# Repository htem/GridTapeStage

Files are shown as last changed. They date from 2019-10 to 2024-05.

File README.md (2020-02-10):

License
-----

Please note the [open-source license](LICENSE.md) before proceeding.

Files
-----

    docs/stage.md: description of stage
    docs/gridtape_stage.png: diagram of stage parts

    docs/protocol.md: description of command protocol and connection info
    docs/commands.md: description of commands, codes and options

    docs/tape_movement.png: diagram of stage movement states and transitions

    software/demo.py: demo python script
    software/temcagt: python control code

    firmware/temcagt_reel: arduino firmware

    docs/parts.xlsx: parts list for orings, fasteners, etc...
    docs/BOM_191002.xlsx: bill of materials including custom parts
    docs/pinouts.xlsx: drive electronics connector pinouts

    hardware/parts: design files for stage parts and assembly
    hardware/drawings: drawings of stage parts

    docs/assembly_instructions.pdf: electronics and hardware assembly
    docs/installation_instructions.pdf: installation instructions

Where to start
-----

Mechanical CAD files were designed in Solidworks and will require a modern (2016+)
version of Solidworks to view.

It's recommended to read through the files in the order they are listed above.

Construction of a stage will require fabricating or purchasing parts found in
the main assembly hardware/parts/xy_v2.SLDASM. Refer to the BOM for a detailed
list of where to purchase and/or how to fabricate components.

See docs/stage.md for a description of the stage.

Extensions to the microcope column (the piezo chamber and reel housings)
should be fabricated, cleaned in a method compatible with a high vacuum system,
assembled with flanges and oring seals and attached to the microscope to
test for leaks. Then, electronics should be added and tape movement tested.
Finally, the piezos, tape channel, pickup rest and a test piece of tape should
be installed to test montaging of tape.

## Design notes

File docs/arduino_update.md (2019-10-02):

Installation
======

IDE
====
The newest version (1.6.11) should be fine.
https://www.arduino.cc/en/Guide/HomePage

Libraries
====
You will also need to install three additional libraries.
https://www.arduino.cc/en/Guide/Libraries  see Manual Installation towards 
the bottom of the page

dSPIN
====
https://github.com/braingram/dSPIN

Comando
====
https://github.com/braingram/comando

HX711
====
https://github.com/bogde/HX711/tree/7ef05358e286980469da54ab3b6235102f44c4f2
The newest commits have changed the way the tension is read so use commit: 7ef05358e286980469da54ab3b6235102f44c4f2

Updating
======
Open the sketch temcagt_reel/temcagt_reel.ino in the Arduino IDE. Make sure 
the electronics are hooked up to the computer. Make sure the correct board 
is selected by checking Tools->Board, it should be something like Arduino Uno.
Make sure the correct port is selected in Tools->Port. Click the upload button.

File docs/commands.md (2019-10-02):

List of commands
------

```
<command_id> : <name> : brief description
    arguments : 
    --
    return values :

0 : error : an error occured in the tape movement
    error code [byte] (see below)

1 : ping : send/receive a simple code (test connection)
    code [byte] : an arbitrary code
    --
    code [byte] : an arbitrary code

5 : read_tension : read n_samples of the tension and return the mean
    n_samples [byte] : number of samples to average
    --
    tension_mean [int32] : result of the average

6 : set_led : set the led brightness
    brightness [byte] : (0 full on, 255 off)

10 : reset_drives : reconfigure all drives

12 : get_status : get the status word for a specific motor
    motor_code [byte] : see below
    --
    status_word [int16] : see below

15 : hold_drive : lock a drive in place
    motor_code [byte] : see below

16 : release_drive : release a drive to allow it to spin freely
    motor_code [byte] : see below

17 : rotate_drive : rotate a drive at a fixed number of steps per second
    motor_code [byte] : see below
    direction [byte] : (0 or 1)
    speed [float] : (steps per second)

18 : set_speed : set the maximum speed of a drive
    motor_code [byte] : see below
    speed [float] : (steps per second)

19 : get_speed : get the maximum speed of a drive
    motor_code [byte] : see below
    --
    speed [float] (steps per second)

20 : move_drive : move a drive a certain number of microsteps
    motor_code [byte] : see below
    direction [byte] : (0 or 1) see below
    n_steps [uint32] : number of microsteps to move

21 : run_reels : rotate both reel motors to take up slack at a fixed rpm
    rpm [float]

22 : stop_reels : stop both reel motors (release them)

23 : stop_all : stop motion of all motors (release reels, hold pinch drives)

24 : release_all : release all motors (allowing them to spin freely)

30 : step_tape : move both pinch drives to advance/retract the tape
    direction [byte] : tape direction
    feed_steps [uint32] : number of microsteps to move feed pinch drive
    pickup_steps [uint32] : number of microsteps to move pickup pinch drive
    time [float] : (seconds) duration of movement
    options [byte] : see below
```

Error Codes
------

- 0 : Error, generic error
- 1 : Missing argument, command call was missing a required argument
- 2 : Invalid argument, a command argument was invalid
- 10 : Invalid drive, a command received an invalid drive motor code
- 11 : Invalid direction, a command received an invalid tape direction

Motor Codes
------

Motor codes are bit fields that determine the side and type of motor to be used in a command. The first bit determines the type (0 reel motor, 1 pinch drive) and second determines the side (0 feed, 1 pickup). In total, the four motors are:

- 0b00 : Feed reel motor
- 0b01 : Feed pinch motor
- 0b10 : Pickup reel motor
- 0b11 : Pickup pinch motor

Tape direction
------

In total there are four tape directions (see 504 in temcagt_reel/reel.ino):

- 0 : Collect, send tape out of a side
- 1 : Dispense, pull tape into a side
- 2 : Tension, pull tape into both sides
- 3 : Untension, send tape out of both sides

Status Word
------

The status word is a 16 bit word read from the motor driver (L6470). See the [L6470 datasheet](www.st.com/resource/en/datasheet/l6470.pdf) for more information.

Step Tape Options
------

The step tape command takes an options byte that currently contains only 1 useful option:

- 0b10 : Wait, wait and report when the tape movement is finished

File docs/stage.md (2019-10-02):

Stage sides
------

The stage is seperated into two parts, a feed side (to the left/front when looking
at the microscope) and a pickup side (to the right/rear). Each side contains
two motors, a pinch drive that can move the tape a linear distance and a reel drive
that rotates to take up extra tape slack during movements.

Stage parts
------

Please see the diagram, gridtape_stage.png.

A. Objective pole piece of microscope
B. Reel motors (outside vacuum)
C. GridTape reels
D. Pinch motors (outside vacuum)
E. Pinch rollers
F. Idle rollers
G. Tension sensor
H. Piezo linear stages
I. Tape channel

The tape path starts at the feed reel (B left), goes between the idle and pinch rollers (E, F), over the tension sensor (G) and into the tape channel (I) that is affixed to the piezo stages (H). While in the channel the tape passes through the objective pole piece (A). From there, the tape exits the channel, enters the pickup pinch drive (right F, E) and is collected onto the pickup reel (right C).

Electronics
------

The stage electronics should be connected in the following order (starting with the power off):

1. connect the stepper motors (these should never be attached or detached when power is on)
2. connect the led and tension sensors (double check they are each in the correct port)
3. connect power
4. connect usb

If power is reset, be sure to disconnect and then reconnect the usb (to reset the arduino).

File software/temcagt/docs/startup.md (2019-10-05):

temcagt nodes are started, stopped and checked using the temcagt script in:

scripts/temcagt

After you install the temcagt python module, this script should be in your
PATH and available for use (note: if the module is installed as an egg-link
by passing -e to pip, you will need to reinstall the temcagt module after any
updates to the temcagt script).

To start the temcagt motion node run:

temcagt start motion

and a similar command for the camera node:

temcagt start camera

Running "temcagt start" without providing any node names will cause the temcagt
script to look in your ~/.temcagt/configs directory for all available node
config files (e.g. ~/.temcagt/configs/motion.json). The temcagt script will then
start all of these nodes in the appropriate order.

After nodes are running, their status can be checked with:

temcagt status

Example output might look like this:

temcagt pids are:
    camera: 22115
    control: 22219
    motion: 22146
    tape: 22189
    ui: 22250

Listing all running nodes and their associated process ids (pids).

To stop the motion node run:

temcagt kill motion

As with temcagt start, temcagt kill can be run with no node names.

If a node fails to kill after several attempts, a more severe stop signal
can be sent using "temcagt kill9". After a kill9 any child processes that
were started by the node will need to be manually killed. For example, if
a camera node fails to shut down after a kill and a kill9 is issued. Run
something like the following to check for remaining processes:

ps aux | grep camera | grep python | grep temcagt

Then kill the process ids using the kill command line tool:

kill 287403

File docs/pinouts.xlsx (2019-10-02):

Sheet: DB-9 pinouts
 | Pin Number | Signal | Stepper wire | Shield Input | Shield | Shield Signal | CS | Chain Index | 0 direction | Enclosure Port
Top DB-9 | 1 | Feed, Pinch | Red | ST2 | Top | 2B | A2 | 0 | CCW | Top
 | 2 | Feed, Pinch | Blue | ST2 | Top | 1B | A2 | 0 | CCW | Top
 | 3 | Feed, Pinch | Black | ST2 | Top | 1A | A2 | 0 | CCW | Top
 | 4 | Feed, Pinch | Green | ST2 | Top | 2A | A2 | 0 | CCW | Top
 | 5 | NC
 | 6 | Feed, Reel | Red | ST2 | Bottom | 2B | D2 | 0 | CCW | Top
 | 7 | Feed, Reel | Blue | ST2 | Bottom | 1B | D2 | 0 | CCW | Top
 | 8 | Feed, Reel | Black | ST2 | Bottom | 1A | D2 | 0 | CCW | Top
 | 9 | Feed, Reel | Green | ST2 | Bottom | 2A | D2 | 0 | CCW | Top
Bottom DB-9 | 1 | Pickup, Pinch | Red | ST1 | Top | 2B | A2 | 1 | CCW | Bottom
 | 2 | Pickup, Pinch | Blue | ST1 | Top | 1B | A2 | 1 | CCW | Bottom
 | 3 | Pickup, Pinch | Black | ST1 | Top | 1A | A2 | 1 | CCW | Bottom
 | 4 | Pickup, Pinch | Green | ST1 | Top | 2A | A2 | 1 | CCW | Bottom
 | 5 | NC
 | 6 | Pickup, Reel | Red | ST1 | Bottom | 2B | D2 | 1 | CCW | Bottom
 | 7 | Pickup, Reel | Blue | ST1 | Bottom | 1B | D2 | 1 | CCW | Bottom
 | 8 | Pickup, Reel | Black | ST1 | Bottom | 1A | D2 | 1 | CCW | Bottom
 | 9 | Pickup, Reel | Green | ST1 | Bottom | 2A | D2 | 1 | CCW | Bottom

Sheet: 4 pin pinouts
 | Pin number | Signal | Buckpuck | Arduino | Load cell | Lemo Pin | Lemo Color
Left 4 pin | 1 | E+ |  |  | Red | 9 | Grey
(above USB) | 2 | E- |  |  | Black | 8 | Violet
 | 3 | A- |  |  | White | 7 | Blue
 | 4 | A+ |  |  | Green | 10 | White
Right 4 pin | 1 | 12V | V+ | -
 | 2 | 5V | REF
 | 3 | D3 | CTL | D3
 | 4 | GND | V- | GND

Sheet: 10pin Lemo
Pin | Wire color | Signal | Load Cell | 4 Pin connector
1 | Black
2 | Brown
3 | Red
4 | Orange
5 | Yellow
6 | Green
7 | Blue | A- | White | 3
8 | Violet | GND (E-) | Black | 2
9 | Gray | 5V (E+) | Red | 1
10 | White | A+ | Green | 4

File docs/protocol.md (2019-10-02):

Hardware Interface
------

The lowest level of interface to the control electronics is a serial
connection running at 115200 baud. A connection to this interface can
be made with pyserial and uses the default connection parameters of

- bytesize=8
- parity='N'
- stopbits=1
- xonxoff=False
- rtscts=False
- dsrdtr=False

```python
import serial

conn = serial.Serial('/dev/ttyACM0', 115200)
```

On connection, the arduino will reset and needs a few (3-4) seconds
to start up before it is able to receive commands.

Message Protocol
------

The serial communication uses a standard message format, part of the
[comando](http://github.com/braingram/comando) library, to allow for
efficient and flexible passing of data back and forth between the
host computer and the control electronics. The low level messages
are described [here](https://github.com/braingram/comando/blob/master/doc/messages.md)
on top of which is built a [protocol format] (https://github.com/braingram/comando/blob/master/doc/protocols.md)
which is used to transmit command following a [command format](https://github.com/braingram/comando/blob/master/doc/commands.md).

These ability to use the same connection for multiple protocols is current not
used. Currently all interaction is through the command protocol which
can be setup as follows:

```python
import pycomando
import serial

conn = serial.Serial('/dev/ttyACM0', 115200)
com = pycomando.Commando(conn)
cmd = pycomando.protocols.CommandProtocol(com)

com.register_protocol(1, cmd)
```

A detailed example of using pycomando commands can be found [here](https://github.com/braingram/comando/blob/master/examples/commands.py). Although the pycomando module is open source,
it is not necessary to use the pycomando module. Briefly, commands can
be sent as follows:

```python
# sent a command of command_id wih 3 arguments (arg0, arg1, arg2)
cmd.send_command(command_id, (arg0, arg1, arg2))

# send a command 0, with args True, 1, 1.5
cmd.send_command(0, (True, 1, 1.5))
```

Receiving commands is done through a callback system.

```python
def ping_received(cmd):
    print("ping received")

# when a command of id 0 is received, call ping_received
cmd.register_callback(0, ping_received)
```

Updating the Comando instance to check for new serial data is done
explicitly by calling: 

```python
com.handle_stream()
```

Additionally, the commands can be called through an EventManager instance
which when initialized with a description of the commands (like that in
the demo, lines 45-142) gives name-based access to commands. For example,
to stop movement of all the motors run:

```python
mgr.trigger('stop_all')
```

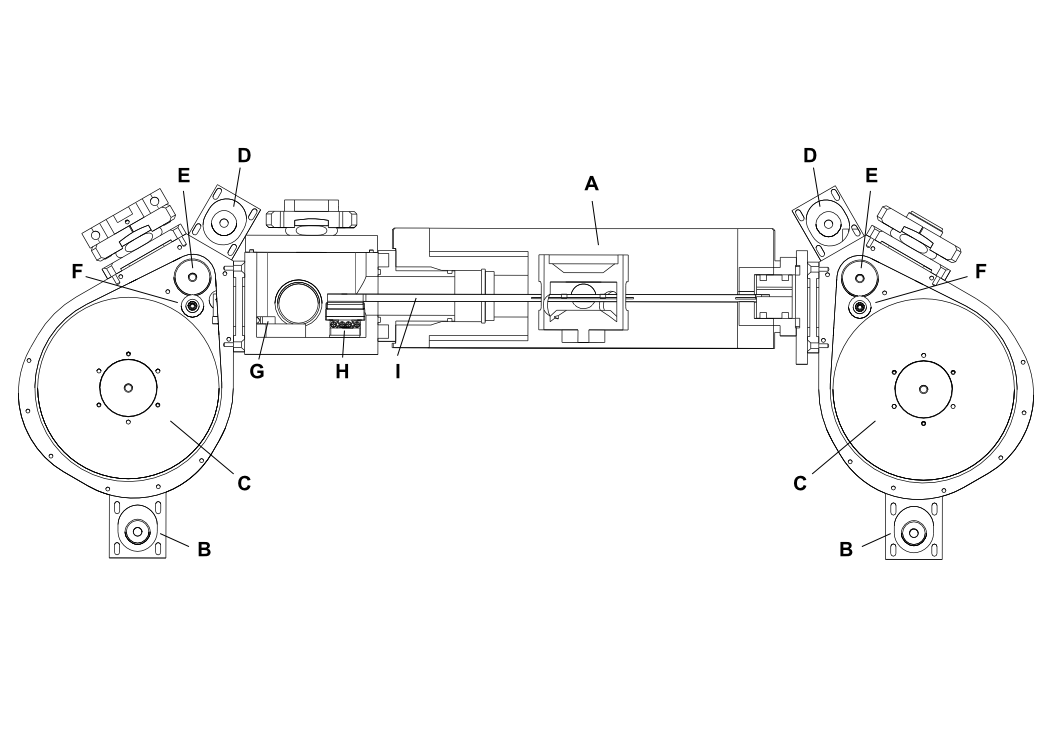
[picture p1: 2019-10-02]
docs/gridtape_stage.png

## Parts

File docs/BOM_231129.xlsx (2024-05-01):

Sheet: BOM
Part name | Quantity | CAD file | Drawing | Assembly | Type | Tested? | Info | Operation | Vender | Part Number | Quantity for 2 | Link | Package Cost | Units per package | Cost (for 1) | Packages for 2 | Cost | Ordered | When
chamber | 1 | chamber_v1 | chamber_v1 | piezo chamber | custom | yes | Al, 2 x 2.25 x 2.938 | machine |  |  | 2
chamber lid | 1 | chamber_lid_with_view | chamber_lid_with_view | piezo chamber | custom | yes | Al, 3/8 x 2 x 2.9063 | machine |  |  | 2
front left flange | 1 | front_left_xy_flange | front_left_xy_flange | piezo chamber | custom |  | Al, 1.6937 x 2 x 2.75 | machine |  |  | 2
piezo baseplate | 1 | piezo_baseplate | piezo_baseplate | piezo stack | custom | yes | Al, 0.049 x 0.669 x 1.181 | machine |  |  | 2
channel baseplate | 1 | channel_base_plate | channel_baseplate | piezo stack | custom | yes | Al, 0.0705 x 0.669 x 0.787 | machine |  |  | 2
load cell baseplate | 1 | load_cell_vertical_base_v2 | load_cell_vertical_base_v2 | tension sensor | custom | yes | Al, 0.295 x 0.570 x 0.875 | machine |  |  | 2
load cell adapter | 1 | tension_roller_mount_v2 | tension_roller_mount_v2 | tension sensor | custom | yes | Al, 0.25 x 0.5 x 0.647 | machine |  |  | 2
load cell rollers | 1 | tension_roller_v2 | tension_roller_v2 | tension sensor | custom | yes | Al, D0.25 x 0.5 | machine |  |  | 2
channel bottom | 1 | straight_stick_v2 | straight_stick_v2 | channel | custom | yes | Al, 1.575 x 0.6693 x 9.75 | machine |  |  | 2
tape clamp | 1 | tape_clamp | tape_clamp | channel | custom | yes | Al, 0.0787 x 0.315 x 9.75 | machine |  |  | 2
takeup reel flange | 1 | takeup_reel_flange | takeup_reel_flange | takeup | custom | yes | Al, 0.25 x 2.5 x 2.5 | machine |  |  | 2
takeup rest static insert | 1 | takeup_rest_insert | takeup_rest_insert | takeup | custom | yes | SS, D1.322 x 0.7874 | machine |  |  | 2
reel housing | 2 | reel_housing | reel_housing | reel housing | custom | yes | Al, 1.25 x 4.625 x 5.8956 | machine |  |  | 4
reel door | 2 | reel_door | reel_door | reel housing | custom | yes | Al, 0.25 x 4.625 x 5.8956 | machine |  |  | 4
reel flange | 2 | reel_housing_flange | reel_housing_flange | reel housing | custom | yes | Al, 0.25 x 2 x 2 | machine |  |  | 4
reel to qf flange | 2 | reel_housing_to_qf16_flange | reel_to_qf16_flange | reel housing | custom | yes | Al, 0.25 x 2 x 2 | machine |  |  | 4
reel blank flange | 4 | reel_housing_blank | reel_housing_blank | reel housing | custom | yes | Al, 0.25 x 1.25 x 2 | machine |  |  | 8
idle roller | 2 | roller | roller | reel housing | custom | yes | Al, D0.5 x 0.4478 | emachineshop |  |  | 4
roller spacer |  | roller_spacer |  | reel housing | custom | yes | Al | machine
inner spacer |  | inner_spacer |  | reel housing | custom | yes | Al | machine
pinch drive roller | 4 | drive_roller | drive_roller | pinch drive | custom | yes | Al, D0.82 x 0.315 | machine |  |  | 8
smaller pinch drive roller | 2 | drive_roller_smaller |  | pinch drive | custom | yes | Al, D0.81 x 0.315 | machine |  |  | 4
pinch drive plate | 2 | pinch_drive_clamp_short |  | pinch drive | custom | yes | Al, 0.125 x 1.1024 x 1.4824 | waterjet |  |  | 4
reel adapter | 2 | reel_adapter_screw_set_3f16 | reel_adapter_screw_set_3f16 | reel drive | custom | yes | Al, D1.675 x 0.5 | machine |  |  | 4
reel drive feedthrough clamp | 4 | ferrotec_clamp | ferrotec_clamp | reel drive | custom | yes | Al, 0.1875 x 1.1024 x 1.1024 | machine |  |  | 8
reel drive plate | 2 | reel_drive_clamp_slipclutch |  | reel drive | custom | yes | Al, 0.125 x 4.4973 x 5.167 | waterjet |  |  | 4
slip clutch shaft | 2 | shaft_adapter_slipclutch | shaft_adapter_slipclutch | reel drive | custom | yes | Al, D0.5 x 1 | machine |  |  | 4
takeup rest oring | 2 |  |  | takeup | oring |  | dash 122 | order | mcmaster | 9464K86 | 4 | http://www.mcmaster.com/#9464K86 | 11.63 | 50 | 0.2326 | 1 | 11.63
piezo chamber lid oring | 1 |  |  | piezo chamber | oring | yes | dash 036 | order | mcmaster | 9464K361 | 2 | http://www.mcmaster.com/#9464K361 | 4.75 | 10 | 0.475 | 1 | 4.75
front left to piezo oring | 1 |  |  | piezo chamber | oring |  | dash 027 | order | mcmaster | 9464K271 | 2 | http://www.mcmaster.com/#9464K271 | 10.76 | 50 | 0.2152 | 1 | 10.76
front left to scope oring | 1 |  |  | piezo chamber | oring |  | dash 028 | order | mcmaster | 9464K281 | 2 | http://www.mcmaster.com/#9464K281 | 10.49 | 50 | 0.2098 | 1 | 10.49
reel flange oring | 6 |  |  | reel housing | oring | yes | dash 027 | order | mcmaster | 9464K271 | 12 | http://www.mcmaster.com/#9464K271 | 10.76 | 50 | 0.2152 | 1 | 10.76
takeup flange oring | 1 |  |  | takeup | oring | yes | dash 219 | order | mcmaster | 9464K41 | 2 | http://www.mcmaster.com/#9464K41 | 11.25 | 25 | 0.45 | 1 | 11.25 |  |  | 92010A001
pinch drive oring | 4 |  |  | pinch drive | oring | yes | dash 018 square | order | mcmaster | 1170N29 | 8 | http://www.mcmaster.com/#1170N29 | 7.94 | 10 | 0.794 | 1 | 7.94 | 6448208 | 2016-03-22
reel housing door oring | 2 |  |  | reel housing | oring | yes | dash 048 | order | mcmaster | 9464K511 | 4 | http://www.mcmaster.com/#9464K511 | 2.23 | 2 | 1.115 | 2 | 4.46 | 6448208 | 2016-03-22
QF-25 clamp | 2 |  |  | piezo chamber | flange | yes |  | order | lesker | QF25-100-C | 4 | http://www.lesker.com/newweb/flanges/hardware_kf_clamps_machined.cfm?pgid=al2 | 8.25 | 1 | 8.25 | 4 | 33 | 6381132 | 160201
QF-25 centering ring | 3 |  |  | piezo chamber | flange | yes |  | order | lesker | QF25-100-SRV | 6 | http://www.lesker.com/newweb/flanges/hardware_kf_centeringrings.cfm?pgid=ss | 8.25 | 1 | 8.25 | 6 | 49.5 | 6381132 | 160201
QF-25 tee | 1 |  |  | piezo chamber | flange | yes |  | order | lesker | QF25-100-T | 2 | http://www.lesker.com/newweb/flanges/fittings_kf_tees.cfm?pgid=standardtee | 75 | 1 | 75 | 2 | 150 | 6381132 | 160201
QF-25 blank flange | 2 |  |  | piezo chamber | flange | yes |  | order | lesker | QF25-100-SB | 4 | http://www.lesker.com/newweb/flanges/flanges_kf_blank.cfm?pgid=flange1 | 9.3 | 1 | 9.3 | 4 | 37.2 | 6381132 | 160201
QF-25 bulkhead clamp | 1 |  |  | piezo chamber | flange | yes |  | order | lesker | QF25-100-BC | 2 | http://www.lesker.com/newweb/flanges/hardware_kf_clamps_bulkhead.cfm?pgid=al | 21.8 | 1 | 21.8 | 2 | 43.6 | 6381132 | 160201
QF-25 feedthrough (smaract) | 1 |  |  | piezo chamber | flange | yes |  | modify | lesker | QF25-100-SB | 2 | http://www.lesker.com/newweb/flanges/flanges_kf_blank.cfm?pgid=flange1 | 9.3 | 1 | 9.3 | 2 | 18.6 | 6381132 | 160201
QF-25 feedthrough (tension) | 1 |  |  | piezo chamber | flange | yes |  | modify | lesker | QF25-100-SB | 2 | http://www.lesker.com/newweb/flanges/flanges_kf_blank.cfm?pgid=flange1 | 9.3 | 1 | 9.3 | 2 | 18.6 | 6381132 | 160201
QF-16 viewport | 3 |  |  | reel housing | flange | yes |  | order | lesker | QF16-075-VP | 6 | http://www.lesker.com/newweb/flanges/viewports_kf_glass.cfm?pgid=0 | 100 | 1 | 100 | 6 | 600 | 6381132 | 160201
QF-16 blank | 3 |  |  | reel housing | flange | yes |  | order | lesker | QF16-075-SB | 6 | http://www.lesker.com/newweb/flanges/flanges_kf_blank.cfm?pgid=flange1 | 8.25 | 1 | 8.25 | 6 | 49.5 | 6381132 | 160201
QF-16 centering ring | 3 |  |  | reel housing | flange | yes |  | order | lesker | QF16-075-SRV | 6 | http://www.lesker.com/newweb/flanges/hardware_kf_centeringrings.cfm?pgid=ss | 6.5 | 1 | 6.5 | 6 | 39 | 6381132 | 160201
QF-16 bulkhead clamp | 3 |  |  | reel housing | flange | yes |  | order | lesker | QF16-075-BC | 6 | http://www.lesker.com/newweb/flanges/hardware_kf_clamps_bulkhead.cfm?pgid=al | 18.6 | 1 | 18.6 | 6 | 111.6 | 6381132 | 160201
tension sensor roller pin | 1 |  |  | tension sensor | fastener | yes | SS, 1/8 x 5/16 dowel pin | order | mcmaster | 90145A878 | 2 | http://www.mcmaster.com/#90145A878 | 7.34 | 50 | 0.1468 | 1 | 7.34
tension sensor adapter screws | 4 |  |  | tension sensor | fastener |  | SS, 0-80 x 1/4 FH | order | mcmaster | 91771A055 | 8 | http://www.mcmaster.com/#91771A055 | 9.01 | 100 | 0.0901 | 1 | 9.01
tension sensor mounting screws | 2 |  |  | tension sensor | fastener | yes | SS, 2-56 x 3/8 SHCS vented | order | mcmaster | 93235A079 | 4 | http://www.mcmaster.com/#93235A079 | 8.12 | 5 | 1.624 | 1 | 8.12 | 6448208 | 2016-03-22
piezo baseplate mounting screws | 4 |  |  | piezo chamber | fastener | yes | SS, 2-56 x 3/16 SHCS vented | order | mcmaster | 93235A076 | 8 | http://www.mcmaster.com/#93235A076 | 5.35 | 5 | 1.07 | 2 | 10.7 | 6448208 | 2016-03-22
piezo stack mounting screws | 4 |  |  | piezo chamber | fastener |  | SS, M1.6 x 4 mm FH | order | mcmaster | 91430A003 | 8 | http://www.mcmaster.com/#91430A003 | 8.7 | 25 | 0.348 | 1 | 8.7 | 6448208 | 2016-03-22
channel plate mounting screws | 2 |  |  | piezo chamber | fastener |  | SS, M2 x 4 mm FH | order | mcmaster | 92010A001 | 4 | http://www.mcmaster.com/#92010A001 | 4 | 100 | 0.04 | 1 | 4
channel mounting screws | 4 |  |  | channel | fastener |  | SS, 0-80 x 7/32 FH | order | mcmaster | 91771A040 | 8 | http://www.mcmaster.com/#91771A040 | 9.63 | 100 | 0.0963 | 1 | 9.63
front left to column screws | 4 |  |  | piezo chamber | fastener |  | SS, M6 x 10 SHCS low profile | order | mcmaster | 92855A610 | 8 | http://www.mcmaster.com/#92855A610 | 8.21 | 25 | 0.3284 | 1 | 8.21 | 6448208 | 2016-03-22
chamber to front left screws | 4 |  |  | piezo chamber | fastener |  | SS, M5 x 16 SHCS | order | mcmaster | 91292A126 | 8 | http://www.mcmaster.com/#91292A126 | 10 | 100 | 0.1 | 1 | 10
chamber lid screws | 4 |  |  | piezo chamber | fastener |  | SS, 6-32 x 1/2 FHSC | order | mcmaster | 92210A148 | 8 | http://www.mcmaster.com/#92210A148 | 4.36 | 100 | 0.0436 | 1 | 4.36
reel flange small screws | 16 |  |  | reel housing | fastener |  | SS, 4-40 x 3/8 FHSC | order | mcmaster | 92210A108 | 32 | http://www.mcmaster.com/#92210A108 | 3.35 | 100 | 0.0335 | 1 | 3.35 | 6448208 | 2016-03-22
reel flange large screws | 16 |  |  | reel housing | fastener |  | SS, 6-32 x 7/16 FHSC | order | mcmaster | 92210A114 | 32 | http://www.mcmaster.com/#92210A114 | 4.38 | 100 | 0.0438 | 1 | 4.38 | 6448208 | 2016-03-22
idle roller shoulder screw | 2 |  |  | pinch drive | fastener |  | SS, 4-40 x 1/8 x 5/8 shoulder screw | modify | mcmaster | 97345A104 | 4 | http://www.mcmaster.com/#97345A104 | 4.39 | 1 | 4.39 | 4 | 17.56 | 6448208 | 2016-03-22
pinch roller set screws | 4 |  |  | pinch drive | fastener |  | SS, 8-32 x 1/4 set screw vented | order | mcmaster | 91979A408 | 8 | http://www.mcmaster.com/#91979A408 | 7.1 | 10 | 0.71 | 1 | 7.1 | 6448208 | 2016-03-22
reel drive set screw | 2 |  |  | reel drive | fastener |  | SS, 8-32 x 1/4 set screw vented | order | mcmaster | 91979A408 | 4 | http://www.mcmaster.com/#91979A408 | 7.1 | 10 | 0.71 | 1 | 7.1 | 6448208 | 2016-03-22
reel hub screws | 6 |  |  | reel drive | fastener |  | SS, 2-56 x 1/2 SHCS | order | mcmaster | 92196A081 | 12 | http://www.mcmaster.com/#92196A081 | 5.72 | 100 | 0.0572 | 1 | 5.72 | 6448208 | 2016-03-22
reel door screws | 20 |  |  | reel housing | fastener | yes | SS, 4-40 x 3/8 SHCS | order | mcmaster | 92196A108 | 40 | http://www.mcmaster.com/#92196A108 | 3.98 | 100 | 0.0398 | 1 | 3.98 | 6448208 | 2016-03-22
ferrotec slamp screws | 16 |  |  | reel housing | fastener |  | SS, 2-56 x 5/16 FHSC | order | mcmaster | 92210A078 | 32 | http://www.mcmaster.com/#92210A078 | 6.22 | 100 | 0.0622 | 1 | 6.22
drive clamp screws | 6 |  |  | reel housing | fastener |  | SS, 4-40 x 3/8 SHCS | order | mcmaster | 92196A108 | 12 | http://www.mcmaster.com/#92196A108 | 3.98 | 100 | 0.0398 | 1 | 3.98 | 6448208 | 2016-03-22
nema 11 screws | 16 |  |  | reel housing | fastener | yes | SS, M2.5 x 6 BHSCS | order | mcmaster | 92095A458 | 32 | http://www.mcmaster.com/#92095A458 | 7.07 | 25 | 0.2828 | 2 | 14.14 | 6448208 | 2016-03-22
slip clutch set screws | 2 |  |  | reel drive | fastener |  | SS, 4-40 x 1/8 set screw | order | mcmaster | 92311A103 | 4 | http://www.mcmaster.com/#92311A103 | 4.21 | 100 | 0.0421 | 1 | 4.21 | 6448208 | 2016-03-22
takeup flange screws | 2 |  |  | takeup | fastener |  | SS, M4 x 10 FHSC | order | mcmaster | 92125A190 | 4 | http://www.mcmaster.com/#92125A190 | 7.23 | 100 | 0.0723 | 1 | 7.23
takeup flange wrench | 1 |  |  | takeup | tool |  | extended t-handle | order | mcmaster | 5334A42 | 2 | http://www.mcmaster.com/#5334A42 | 1.97 | 1 | 1.97 | 2 | 3.94 | 6448208 | 2016-03-22
stepper motors | 4 |  |  | motors | motors |  | nema 11 stepper | order | digikey | 1460-1072-ND | 8 | http://www.digikey.com/product-search/en?keywords=1460-1072-nd | 37.99 | 1 | 37.99 | 8 | 303.92 | 6390515 | 160208
tension sensor | 1 |  |  | tension sensor | sensor |  | 0-100g load cell | modify | phidgets | CZL639HD | 2 | http://www.phidgets.com/products.php?category=34&product_id=3139_0 | 7 | 1 | 7 | 2 | 14 | pcard | 160205
ferrotec feedthrough | 4 |  |  | reel housing | feedthrough | yes | rotary feedthroughs |  | ferrotec | 103073 | 8 | https://www.ferrotec.com/index.php?id=feedthrough_detail&vfp_id=34 | 600 | 1 | 600 | 8 | 4800 | 6382708 | 160202
piezo xy stack | 1 |  |  | piezo stack | motors |  | slc-1720-s-hv, in xy, with MCS | order | smaract | slc-1720-s-hv | 2 | http://smaract.de/index.php/products/slc17-positioners/slc-1720 | 9052.5 | 1 | 9052.5 | 2 | 18105 | 6382658 | 160202
load cell amplifier | 1 |  |  | electronics | electronics |  | load cell amplifier | modify | sparkfun | SEN-13230 | 2 | https://www.sparkfun.com/products/13230 | 9.95 | 1 | 9.95 | 2 | 19.9
microcontroller proto board | 1 |  |  | electronics | electronics |  | arduino protoshield | modify | sparkfun | DEV-11665 | 1 | https://www.sparkfun.com/products/11665 | 4.95 | 1 | 4.95 | 1 | 4.95
stepper motor driver shield | 2 |  |  | electronics | electronics |  | x-nucleo-ihm02a1 | modify | digikey | 497-16251-ND | 4 | https://punchout.digikey.com/scripts/DkSearch/dksus.dll?Detail&itemSeq=191838508&uq=635932000139947652 | 14.16 | 1 | 14.16 | 4 | 56.64 | 6432645 | 160310
power supply | 1 |  |  | electronics | electronics |  | 12V >3A supply | order | digikey | 237-1443-ND | 2 | http://www.digikey.com/product-detail/en/WSU120-3000/237-1443-ND/3094969 | 20.27 | 1 | 20.27 | 2 | 40.54 | 6390515 | 160208
power jack | 1 |  |  | electronics | electronics |  | barrel jack | modify | digikey | CP-065A-ND | 2 | http://www.digikey.com/product-search/en?keywords=CP-065A-ND | 2.54 | 1 | 2.54 | 2 | 5.08 | 6390515 | 160208
microcontroller | 1 |  |  | electronics | electronics |  | arduino | modify | digikey | 1050-1041-ND | 2 | http://www.digikey.com/product-detail/en/A000073/1050-1041-ND/3476357 | 21.54 | 1 | 21.54 | 2 | 43.08 | 6390515 | 160208
tension sensor cabling | 1 |  |  | electronics | electronics |  | 10 conductor wiring | modify | digikey | W410-50-ND | 1 | http://www.digikey.com/product-search/en?keywords=w410-50-nd | 64.63 | 1 | 64.63 | 1 | 64.63 | 6390515 | 160208
tension sensor feedthrough | 1 |  |  | electronics | electronics |  | lemo feedthrough | modify | mouser | 736-HGP2S310CLLPV | 2 | http://www.mouser.com/ProductDetail/LEMO/HGP2S310CLLPV/ | 102.14 | 1 | 102.14 | 2 | 204.28 | pcard | 160208
tension sensor connector | 1 |  |  | electronics | electronics |  | lemo plug | modify | mouser | 736-FFP2S310CLAC72Z | 2 | http://www.mouser.com/ProductDetail/LEMO/FFP2S310CLAC72Z/ | 70.11 | 1 | 70.11 | 2 | 140.22 | pcard | 160208
idle roller bearing | 4 |  |  | pinch drive | mechanics |  | 1/8 shaft 1/4 flanged bearing | order | mcmaster | 57155k205 | 8 | http://www.mcmaster.com/#57155K205 | 5.71 | 1 | 5.71 | 8 | 45.68 | 6448208 | 2016-03-22
pinch drive timing belt pulley | 4 |  |  | pinch drive | mechanics |  | 1/8 MXL 15 tooth 3/16 bore | modify | mcmaster | 1375K15 | 8 | http://www.mcmaster.com/#1375K15 | 9.81 | 1 | 9.81 | 4 | 39.24 | 6448208 | 2016-03-22
reel drive timing belt pulley | 2 |  |  | reel drive | mechanics |  | 1/8 MXL 15 tooth 3/16 bore | modify | mcmaster | 1375K15 | 4 | http://www.mcmaster.com/#1375K15 | 9.81 | 1 | 9.81 | 2 | 19.62 | 6448208 | 2016-03-22
slip clutch timing belt pulley | 2 |  |  | reel drive | mechanics |  | 1/8 MXL 18 tooth 3/16 bore | modify | mcmaster | 1375K17 | 4 | https://www.mcmaster.com/1375K17/ | 12.92 | 1 | 12.92 | 4 | 51.68
pinch drive timing belt | 1 |  |  | pinch drive | mechanics |  | MXL 1/8" Width, 4" Outer Circle | order | mcmaster | 7887K12 | 2 | http://www.mcmaster.com/#7887K12 | 2.39 | 1 | 2.39 | 2 | 4.78 | 6448208 | 2016-03-22
reel drive timing belt | 1 |  |  | reel drive | mechanics |  | MXL 1/8" Width, 7.6" Outer Circle | order | mcmaster | 7887K19 | 2 | http://www.mcmaster.com/#7887K19 | 2.51 | 1 | 2.51 | 2 | 5.02 | 6448208 | 2016-03-22
slip clutch | 2 |  |  | reel drive | mechanics |  | 0.25" Bore Adjustable Slip Clutch with Torque Range of .3 to 32 OZ-IN | order | SDP/SI | S98CA6-MEC160417 | 4 | https://shop.sdp-si.com/catalog/product/?id=S98CA6-MEC160417 | 64.59 | 1 | 64.59 | 2 | 129.18
tape camera | 1 |  |  | electronics | electronics |  | raspberry pi or m12 | order |  |  | 2 |  |  | 1 | 0 | 2 | 0
tape camera mount | 1 | picam_to_viewport_mount |  | tape camera | mechanics |  |  | 3d print |  |  | 2 |  | 0 | 1 | 0 | 2 | 0
light led | 1 |  |  | electronics | electronics |  |  | order | digikey |  | 2 |  |  | 1 | 0 | 2 | 0
light heatsink | 1 |  |  | electronics | electronics |  |  | order | digikey | 345-1105-ND | 2 | http://www.digikey.com/product-detail/en/882-100AB/345-1105-ND/2640528 | 2.34 | 1 | 2.34 | 2 | 4.68 | 6390515 | 160208
light driver | 1 |  |  | electronics | electronics |  |  | order | digikey | 788-1096-ND | 2 | http://www.digikey.com/product-detail/en/3021-D-I-700/788-1096-ND/3114413 | 16.99 | 1 | 16.99 | 2 | 33.98 | 6390515 | 160208
tc led mount | 1 | tc led mount |  |  | electronics |  |  | 3d print |  |  | 2 |  | 0 | 1 | 0 | 2 | 0
case | 1 |  |  | electronics | electronics |  |  | modify | digikey | HM856-ND | 2 | https://punchout.digikey.com/scripts/DkSearch/dksus.dll?Detail&itemSeq=193471005&uq=635950280810903346 | 7.94 | 1 | 7.94 | 2 | 15.88
db9 connector | 2 |  |  | electronics | electronics |  |  | order | digikey | L77SDE09S-ND | 4 | https://www.digikey.com/en/products/detail/amphenol-cs-commercial-products/L77SDE09S/1930962
db9 case | 1 |  |  | electronics | electronics |  |  | order | digikey | 116-40-9709H-ND | 2 | https://www.digikey.com/en/products/detail/cinch-connectivity-solutions/40-9709H/3830261
4 pin molex connector | 2 |  |  | electronics | electronics |  |  | order | digikey | 23-0022057045-ND | 4 | https://www.digikey.com/en/products/detail/molex/0022057045/403343
4 pin molex connector | 2 |  |  | electronics | electronics |  |  | order | digikey | WM17405-ND | 4 | https://www.digikey.com/en/products/detail/molex/0050375043/259392
molex crimps | 100 |  |  | electronics | electronics |  |  | order | digikey | WM18889CT-ND | 200 | https://www.digikey.com/en/products/detail/molex/0008701039/765268
7pos housing receptacle |  |  |  | electronics | electronics |  |  | order | digikey | 952-2232-ND | 25 | https://www.digikey.com/en/products/detail/harwin-inc/M20-1060700/3728196?s=N4IgTCBcDaILZgAwFoCMiBsiDsIC6AvkA
Harwin crimps |  |  |  | electronics | electronics |  |  | order | digikey | 952-2157-1-ND | 200 | https://www.digikey.com/en/products/detail/harwin-inc/M20-1160042/3728123

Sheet: Piezo Chamber
Part name | Info | Quantity | CAD file | Modification? | Vender | Part Number | Link | Package Cost | Units per package | Cost (for 1) | Cost | Ordered | When
chamber | Sheet 2 1/2 x 3 x 4 Al | 1 | chamber_v1 | Yes | mcmaster |  |  |  | 1 |  | #VALUE! | Yes | 150326
chamber lid | Sheet 3/8 x 2 1/2 x 6 Al | 1 | chamber_lid_with_view | Yes | mcmaster |  |  |  | 2 |  | #VALUE! | Yes | 150326
piezo baseplate | Sheet 1/8 x 1 x 6 Al | 1 | piezo_baseplate | Yes | mcmaster | 8975K578 | http://www.mcmaster.com/#8975k578 | 0.86 | 3 | $0.29 | $0.29 | Yes | stock
load cell baseplate | Sheet 1/2 x 1/2 x 6 Al | 1 | load_cell_vertical_base_v2 | Yes | mcmaster | 9008K81 | http://www.mcmaster.com/#9008k81 | 1.48 | 6 | $0.25 | $0.25 | Yes | stock
load cell wall | Sheet 0.032 x 2 x 24 Al | 2 | load_cell_plate | Yes | mcmaster | 89015k151 | http://www.mcmaster.com/#89015k151 | 5.2 | 24 | $0.22 | $0.43 | Yes | stock
load cell adapter | Sheet 1/2 x 1/2 x 6 Al | 1 | load_cell_roller_mount_v2 | Yes | mcmaster | 9008K81 | http://www.mcmaster.com/#9008k81 | 1.48 | 6 | $0.25 | $0.25 | Yes | stock
idle roller | Rod 5/16 x 6 Al | 2 | tension_roller_v2 | Yes | mcmaster | 8974k23 | http://www.mcmaster.com/#8974k23 | 1.9 | 6 | $0.32 | $0.63 | Yes | 150326
 |  | 1 | front_left_xy_flange
takeup rest | Rod 1 3/16 x 6 Al | 1 | takeup_rest_insert | Yes | mcmaster | 8974k17 | http://www.mcmaster.com/#8974k17 | 10.26 | 3 | $3.42 | $3.42
 |  |  | takeup_rest_body
 |  |  | takeup_rest_slider
channel bottom | Sheet 3/4 x 1 x 12 Al | 1 | straight_stick_v2 | Yes | mcmaster | 8975k11 | http://www.mcmaster.com/#8975k11 | 5.14 | 1 | $5.14 | $5.14 | Yes | 150401
 |  |  | channel_base_plate
channel top | Sheet 3/4 x 1 x 12 Al | 1 | tape_clamp | Yes | mcmaster | 8975k11 | http://www.mcmaster.com/#8975k11 | 5.14 | 1 | $5.14 | $5.14 | Yes | 150401
channel clamps | Shim 0.005 SS | 1 |  | Yes | mcmaster |  |  |  |  |  | #VALUE! | Yes | stock
-- fasteners -- |  |  |  |  |  |  |  |  |  |  | #VALUE!
tension roller pin
chamber mounting screws | M5 x 16 | 4 |  |  | mcmaster | 91292a126 | http://www.mcmaster.com/#91292a126 | 10 | 100 | $0.10 | $0.40 | Yes | stock
chamber lid screws | #6 x 1/2 fhsc | 4 |  |  | mcmaster | 92210a148 | http://www.mcmaster.com/#92210a148 | 4.92 | 100 | $0.05 | $0.20 | Yes | 150326
piezo baseplate screws | 2-56 x 3/16 sc vented | 4 |  |  | mcmaster | 93235a076 | http://www.mcmaster.com/#93235a076 | 5.35 | 5 | $1.07 | $4.28 | Yes | 150326
load cell wall screws | 0-80 x 1/8 sc | 4 |  | Yes | mcmaster | 92210a010 | http://www.mcmaster.com/#92210a010 | 4.58 | 50 | $0.09 | $0.37 | Yes | 150326
load cell base screws | 2-56 x 1/2 sc vented | 2 |  |  | mcmaster | 93235a081 | http://www.mcmaster.com/#93235a081 | 14.07 | 5 | $2.81 | $5.63 | Yes | stock
load cell adapter screws | 0-80 x 1/4 sc | 4 |  | Yes | mcmaster | 90585a017 | http://www.mcmaster.com/#90585a017 | 7.51 | 12 | $0.63 | $2.50 | Yes | 150326
channel mount screws | M2 x 3 fhsc | 2 |  |  | mcmaster | 93395a135 | http://www.mcmaster.com/#93395a135 | 4.6 | 25 | $0.18 | $0.37 | Yes | 150401
channel clamp screws | 0-80 x 1/16 sc | 4 |  | Yes | mcmaster | 92196a047 | http://www.mcmaster.com/#92196a047 | 8.35 | 50 | $0.17 | $0.67 | Yes | 150401
-- orings -- |  |  |  |  |  |  |  |  |  |  | #VALUE!
takeup rest oring | dash 123 |  |  |  | mcmaster | 9464k87 | http://www.mcmaster.com/#9464k87 | 6.6 | 25 | $0.26 | $0.00
chamber lid oring | dash 036 | 1 |  |  | mcmaster | 9464k361 | http://www.mcmaster.com/#9464k361 | 4.75 | 10 | $0.47 | $0.47 | Yes | 150326
front port coupler oring | dash 028
-- misc -- |  |  |  |  |  |  |  |  |  |  | #VALUE!
piezo xy plate |  |  |  |  |  |  |  |  |  |  | #VALUE!
load cell |  |  |  |  |  |  |  |  |  |  | #VALUE!
-- vacuum flanges -- |  |  |  |  |  |  |  |  |  |  | #VALUE!
QF-25 clamp |  |  |  |  |  |  |  |  |  |  | #VALUE!
QF-25 centering ring |  |  |  |  |  |  |  |  |  |  | #VALUE!
QF-25 blank flange |  |  |  |  |  |  |  |  |  |  | #VALUE!
QF-25 tee |  |  |  |  |  |  |  |  |  |  | #VALUE!
QF-25 bulkhead connector |  | 1 |  |  | lesker | QF25-100-BC | http://www.lesker.com/newweb/flanges/hardware_kf_clamps_bulkhead.cfm?pgid=al | 21.8 | 1 | $21.80 | $21.80
-- electronics -- |  |  |  |  |  |  |  |  |  |  | #VALUE!
Load cell |  | 1 |  |  | phidgets | CZL639HD |  | 7 | 1 | $7.00 | $7.00
Load cell amplifier |  | 1 |  |  | sparkfun | SEN-13230 |  | 9.95 | 1 | $9.95 | $9.95
Piezos |  |  | xy_slc-1720-s_v2 |  | smaract |  |  | 22454.73 | 1 | $22454.73 | $0.00

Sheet: Reel housing
Part name | Info | Quantity | CAD file | Modification? | Vender | Part Number | Link | Package Cost | Units per package | Cost (for 1) | Cost | Ordered | When
Housing | Sheet 1 1/2 x 6 x 12 Al | 1 | reel_housing | Yes | mcmaster | 8975K336 | http://www.mcmaster.com/#8975K336 | 79.17 | 2 | $39.59 | $39.59 | Yes | 150401
Door | Sheet 1/4 x 6 x 12 Al (flat) | 1 | reel_door | Yes | mcmaster | 3511t12 | http://www.mcmaster.com/#3511t12 | 52.19 | 2 | $26.09 | $26.09 | Yes | 150401
Reel flange | Sheet 1/4 x 2 x 12 Al (flat) | 1 | reel_housing_flange | Yes | mcmaster | 3511t111 | http://www.mcmaster.com/#3511t111 | 34.79 | 5 | $6.96 | $6.96 | Yes | 150326
Reel to qf flange | Sheet 1/4 x 2 x 12 Al (flat) | 1 | reel_housing_to_qf16_flange | Yes | mcmaster | 3511t111 | http://www.mcmaster.com/#3511t111 | 34.79 | 5 | $6.96 | $6.96 | Yes | 150326
Reel blank flange | Sheet 1/4 x 2 x 12 Al (flat) | 1 | reel_housing_blank | Yes | mcmaster | 3511t111 | http://www.mcmaster.com/#3511t111 | 34.79 | 8 | $4.35 | $4.35 | Yes | 150326
Idle roller | Rod 1/2 x 6 Al | 1 | roller | Yes | mcmaster | 8974k28 | http://www.mcmaster.com/#8974k28 | 2.3 | 6 | $0.38 | $0.38 | Yes | stock
Idle roller spacer | Rod 3/16 x 12 Al | 1 |  | Yes | mcmaster | 8974K21 | http://www.mcmaster.com/#8974K21 | 1.47 | 6 | $0.24 | $0.24 | Yes | 150326
Reel adapter | Rod 1 5/8 x 6 Al | 1 | reel_adapter_screw_set_3f16 | Yes | mcmaster | 8974k66 | http://www.mcmaster.com/#8974k66 | 13.12 | 6 | $2.19 | $2.19 | Yes | stock
Pinch driver roller | Rod 7/8 x 6 Al | 1 | drive_roller | Yes | mcmaster | 8974K12 | http://www.mcmaster.com/#8974K12 | 4.99 | 6 | $0.83 | $0.83 | Yes | stock
Pinch drive plate | Sheet 1/4 x 1 1/4 x 6 Al | 1 | pinch_drive_clamp | Yes | mcmaster | 8975K597 | http://www.mcmaster.com/#8975K597 | 2.21 | 2 | $1.10 | $1.10 | Yes | stock
 |  |  | reel_drive_clamp
Takeup reel flange | Sheet 5/16 x 3 x 6 Al | 1 | takeup_reel_flange | Yes | mcmaster | 8975k89 | http://www.mcmaster.com/#8975k89 | 5.96 | 4 | $1.49 | $1.49 | Yes | 150326
-- fasteners -- |  |  |  |  |  |  |  |  |  |  | #VALUE!
Reel guide shoulder screws | 4-40, 1/8 x 5/8 shoulder screw | 2 |  |  | mcmaster | 97345a104 | http://www.mcmaster.com/#97345a104 | 4.39 | 1 | $4.39 | $8.78 | Yes | stock
Ferrotec clamp screws | 2-56 x 1/4 fhsc | 8 |  |  | mcmaster | 92210a077 | http://www.mcmaster.com/#92210a077 | 6.72 | 100 | $0.07 | $0.54 | Yes | 150401
Reel flange clamp screws | 4-40 x 3/8 fhsc | 8 |  |  | mcmaster | 92210a108 | http://www.mcmaster.com/#92210a108 | 3.88 | 100 | $0.04 | $0.31 | Yes | 150326
Reel door clamp screws | 4-40 x sc | 10 |  |  | mcmaster | 92196a108 | http://www.mcmaster.com/#92196a108 | 4.12 | 100 | $0.04 | $0.41 | Yes | stock
Reel and drive set screws | 8-32 x 3/16 set screw vented | 4 |  |  | mcmaster | 91979a403 | http://www.mcmaster.com/#91979a403 | 6.61 | 10 | $0.66 | $2.64 | Yes | stock
Reel screws | 2-56 x 1/2 fhsc | 3 |  |  | mcmaster | 92210a081 | http://www.mcmaster.com/#92210a081 | 10.28 | 100 | $0.10 | $0.31 | Yes | 150326
Takeup flange screws | M4 x 10 fhsc | 2 |  |  | mcmaster | 92125a190 | http://www.mcmaster.com/#92125a190 | 7.23 | 100 | $0.07 | $0.14 | Yes | 150326
Reel plate mounting screw | #6 x 7/16 fhsc | 4 |  |  | mcmaster | 92210a114 | http://www.mcmaster.com/#92210a114 | 4.96 | 100 | $0.05 | $0.20 | Yes | 150401
-- orings -- |  |  |  |  |  |  |  |  |  |  | #VALUE!
Door oring | dash 048 | 1 |  |  | mcmaster | 9464k511 | http://www.mcmaster.com/#9464K511 | 2.23 | 2 | $1.11 | $1.11 | Yes | 150326
Reel flange oring | dash 027 | 3 |  |  | mcmaster | 9464k271 | http://www.mcmaster.com/#9464k271 | 10.76 | 50 | $0.22 | $0.65 | Yes | stock
Pinch drive oring | dash 018 square | 2 |  |  | mcmaster | 1170N29 | http://www.mcmaster.com/#1170N29 | 7.94 | 10 | $0.79 | $1.59 | Yes | 150326
Takeup flange oring | dash 219 | 1 |  |  | mcmaster | 9464k41 | http://www.mcmaster.com/#9464k41 | 11.25 | 25 | $0.45 | $0.45 | Yes | 150326
-- misc -- |  |  |  |  |  |  |  |  |  |  | #VALUE!
Idle roller bearing | 1/8 shaft 1/4 flanged bearing | 2 |  |  | mcmaster | 57155k205 | http://www.mcmaster.com/#57155k205 | 5.71 | 1 | $5.71 | $11.42 | Yes | stock
Pinch timing belt | MXL 1/8" Width, 4" Outer Circle | 1 |  |  | mcmaster | 7887K12 | http://www.mcmaster.com/#7887K12 | 2.39 | 1 | $2.39 | $2.39
Reel timing belt | MXL 1/8" Width, 7.6" Outer Circle | 1 |  |  | mcmaster | 7887K19 | http://www.mcmaster.com/#7887K19 | 2.51 | 1 | $2.51 | $2.51
Timing belt pulley | 1/8 MXL 15 tooth 3/16 bore | 3 |  |  | mcmaster | 1375K15 | http://www.mcmaster.com/#1375K15 | 9.81 | 1 | $9.81 | $29.43 | Yes | 150326
Slip clutch pulley
Slip clutch shaft collar
Slip clutch washers
Slip clutch spring washer
Slip clutch shaft
-- vacuum flanges -- |  |  |  |  |  |  |  |  |  |  | #VALUE!
QF-16 viewport |  | 1 |  |  | lesker | QF16-075-VP | http://www.lesker.com/newweb/flanges/viewports_kf_glass.cfm?pgid=0 | 100 | 1 | $100.00 | $100.00 | Yes | stock
QF-16 bulkhead connector |  | 1 |  |  | lesker | QF16-075-BC | http://www.lesker.com/newweb/flanges/hardware_kf_clamps_bulkhead.cfm?pgid=al | 18.6 | 1 | $18.60 | $18.60 | Yes | stock
QF-16 oring |  | 1 |  |  |  |  |  |  |  |  | #VALUE! | Yes | stock
QF-16 clamp |  |  |  |  |  |  |  |  |  |  |  | Yes | stock
-- electronics -- |  |  |  |  |  |  |  |  |  |  | #VALUE!
Stepper motors | nema 11 | 2 | nema11 |  | pololu | 1206 |  | 19.95 | 1 | $19.95 | $39.90 | Maybe
Camera |  | 1 |  |  | point grey |  |  | $1105 | 1 | $1105.00 | $1105.00
Motor drivers |  | 2 |  |  | sparkfun | BOB-11611 |  | 34.95 | 1 | $34.95 | $69.90
Microcontroller |  | 1 |  |  | sparkfun | DEV-11021 |  | 24.95 | 1 | $24.95 | $24.95

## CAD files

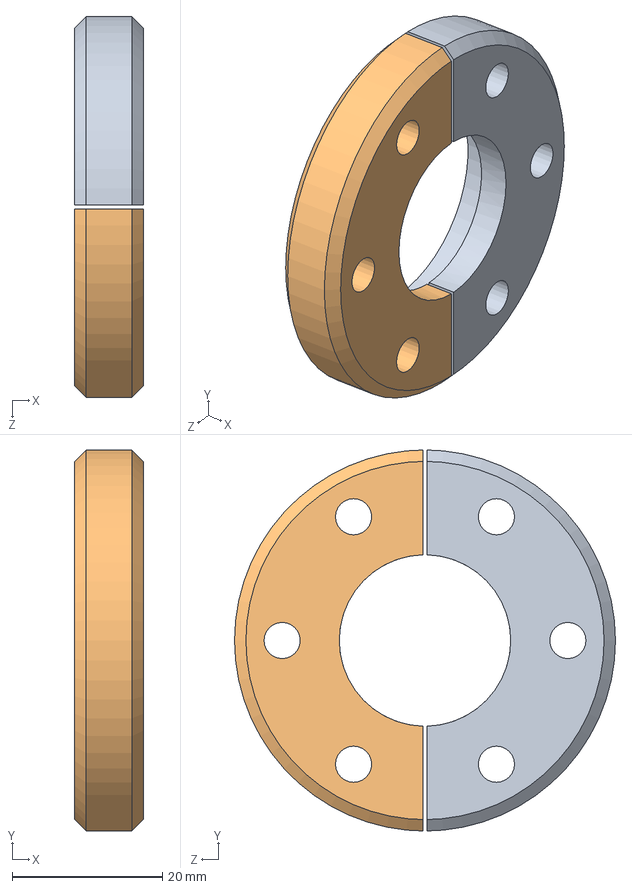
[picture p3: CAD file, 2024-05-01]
hardware/parts/other/QF16-075-BC_1.sldasm
9.17 x 50.8 x 50.8 mm
QF16-075-BC-R_2
QF16-075-BC-R_3

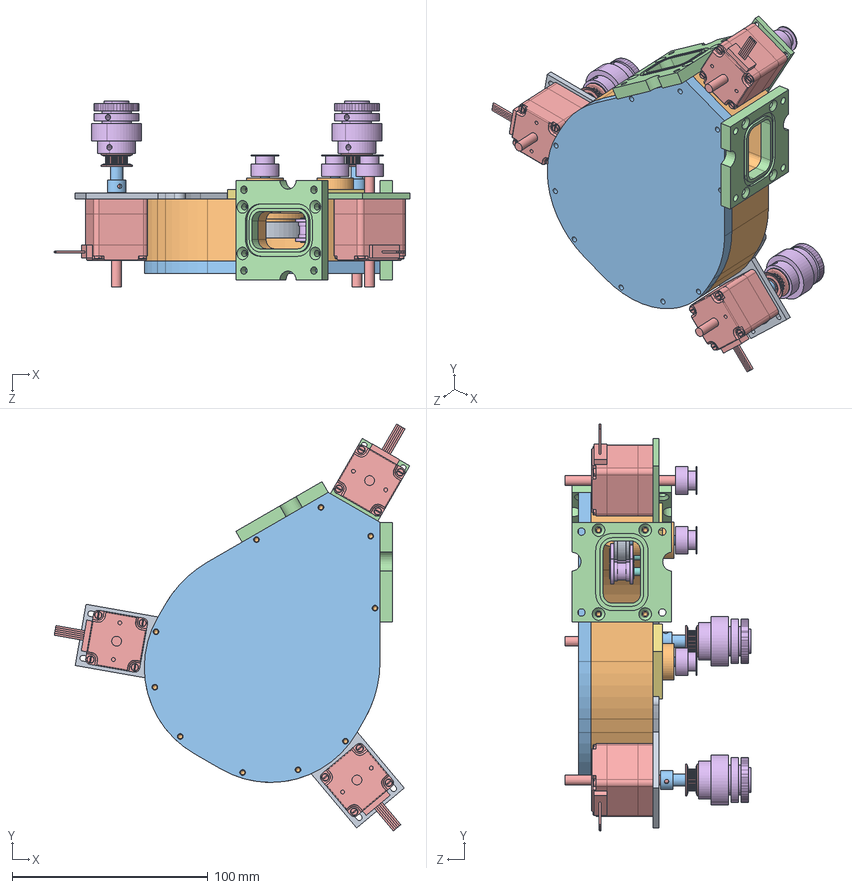
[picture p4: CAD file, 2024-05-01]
hardware/parts/test_fit1.sldasm
181.6 x 207.8 x 95.2 mm
reel_hub
101920 render x 2
116906 render x 2
101649 render x 2
100517 render x 2
roller x 2
57155K205 x 4
inner_spacer x 2
drive_roller
reel_housing
reel_housing_flange x 2
nema11 x 3
mxl_15t_3f16b_1375K15 x 3
ferrotec_clamp x 2
roller_spacer x 2
reel_drive_clamp_slipclutch x 2
reel_adapter_screw_set_3f16
shaft_adapter_slipclutch x 2
pinch_drive_clamp_short
bandbmnfg_18mp012-6fa2 x 2
SI_sdpsi_s98ca6-mec160417.stp x 2

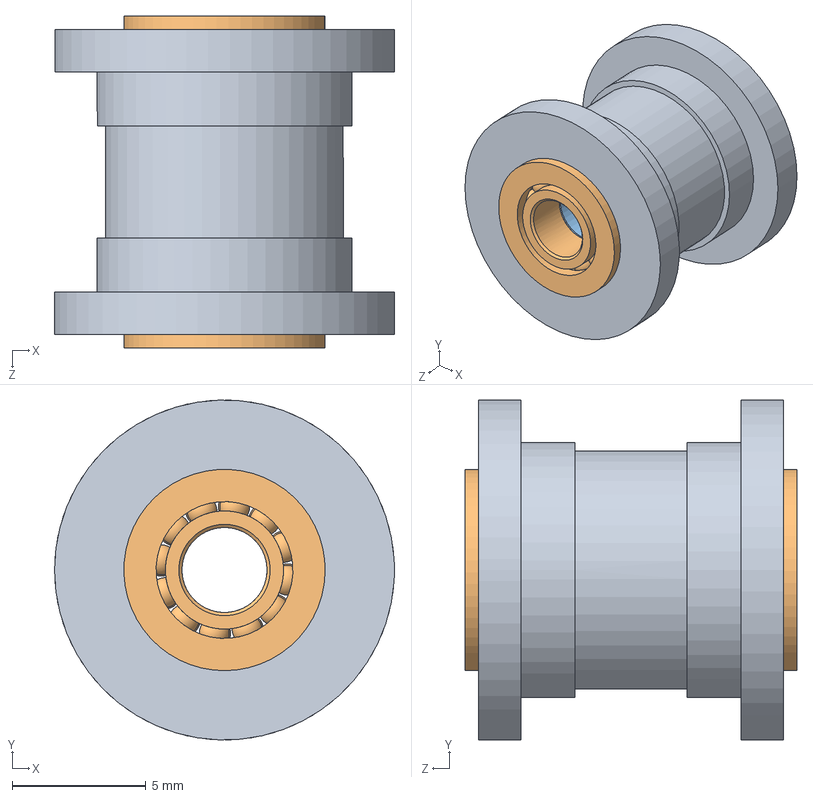
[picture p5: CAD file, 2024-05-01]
hardware/parts/other/machined_roller_no_shaft.SLDASM
12.7 x 12.7 x 12.4 mm
roller
57155K205 x 2
inner_spacer

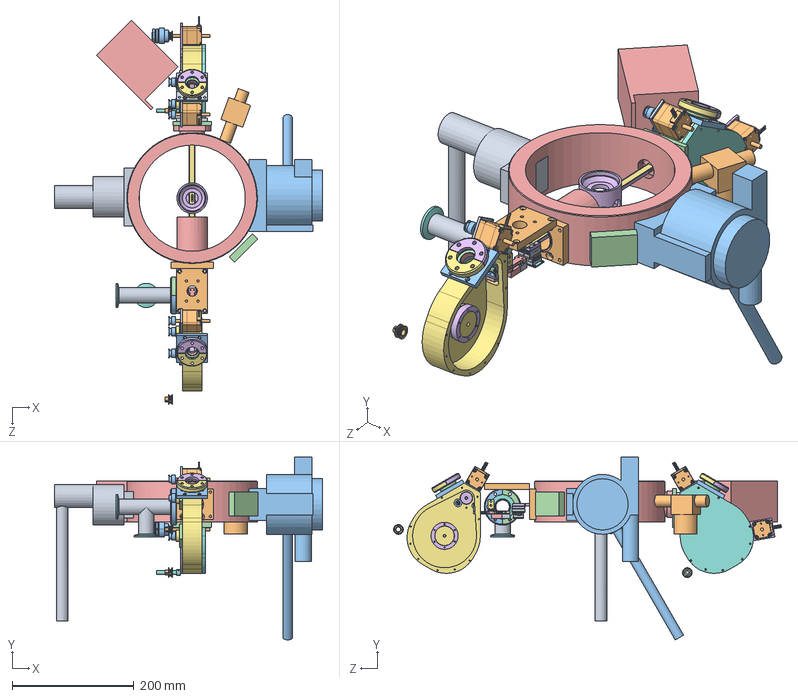
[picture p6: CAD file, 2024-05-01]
hardware/parts/xy_v2.SLDASM
440.1 x 300.2 x 636.8 mm
goniometer_2
right_side_solenoid
goniometer
aperture_objective_plate
JEOL 1200EX OL Module Rev. B
sap
Aperture blade
piezo_baseplate
smaract_slc1720s x 2
XY_SLC-1720-s_V2
tension_roller_mount_v2
tension_roller_v2
100g_load_cell_RB-Phi-203
load_cell_vertical_base_v2
reel_hub x 2
101920 render x 4
116906 render x 4
101649 render x 4
100517 render x 4
drive_roller x 2
reel_housing x 2
roller x 2
57155K205 x 4
inner_spacer x 2
reel_housing_flange x 2
nema11 x 2
mxl_15t_3f16b_1375K15 x 6
ferrotec_clamp x 4
reel_adapter_screw_set_3f16 x 2
pinch_drive_clamp_short x 2
bandbmnfg_18mp012-6fa2 x 2
takeup_reel_flange
takeup_rest_insert
straight_stick_v2
tape_clamp
bent_spring_clamp x 3
spring_clamp
channel_base_plate
reel_housing_to_qf16_flange x 2
C0001197 x 2
P0001219 x 2
QF16-075-BC-R_2 x 2
QF16-075-BC-R_3 x 2
P0001498 x 3
P0017967
front_left_xy_flange

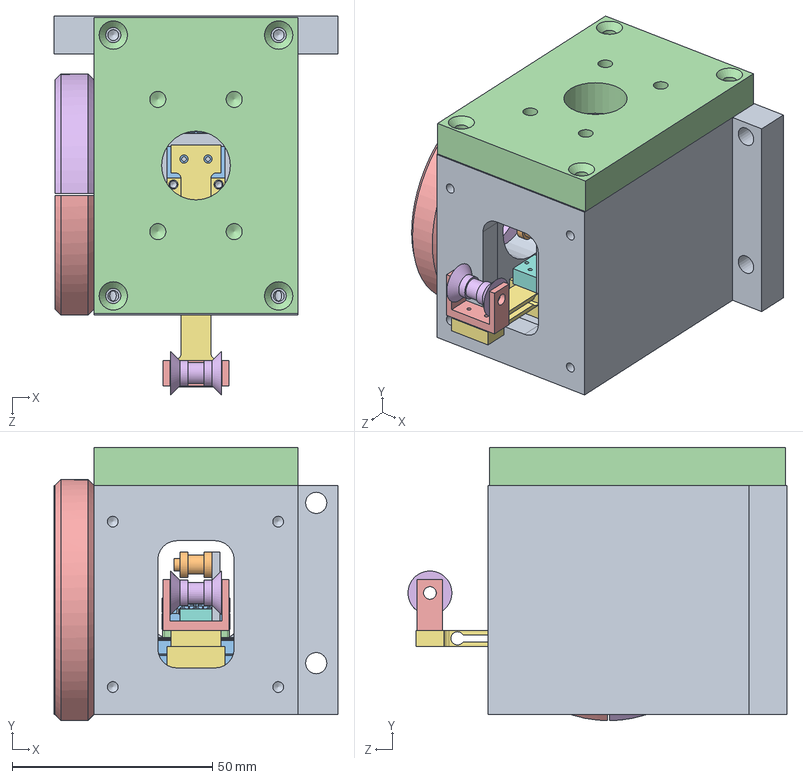
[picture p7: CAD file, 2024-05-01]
hardware/parts/piezo_chamber.SLDASM
70.8 x 68.2 x 94.6 mm
chamber_v1
piezo_baseplate
smaract_slc1720s x 2
XY_SLC-1720-s_V2
tension_roller_mount_v2
tension_roller_v2
100g_load_cell_RB-Phi-203
load_cell_vertical_base_v2

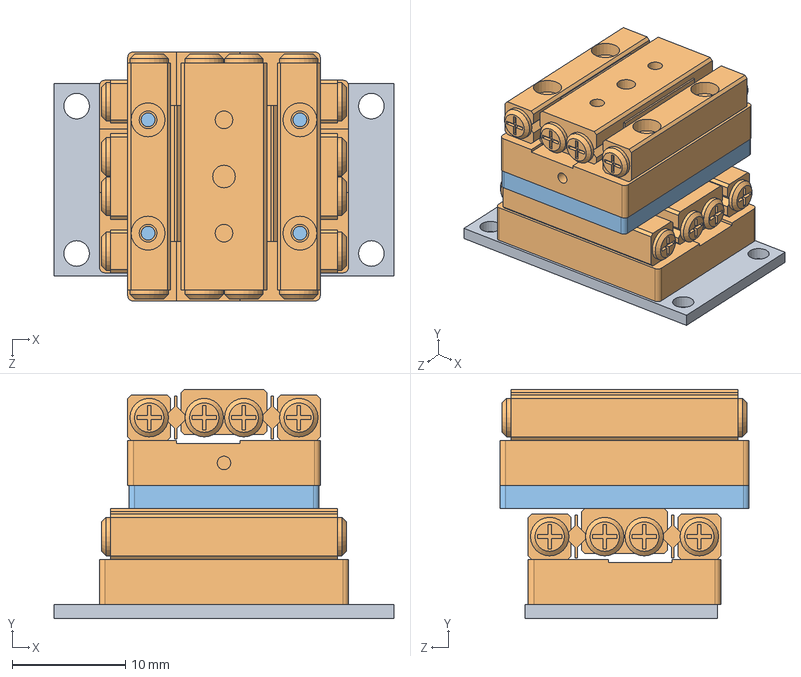
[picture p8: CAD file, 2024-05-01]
hardware/parts/piezo_stack.SLDASM
30.0 x 20.2 x 22.0 mm
piezo_baseplate
smaract_slc1720s x 2
XY_SLC-1720-s_V2

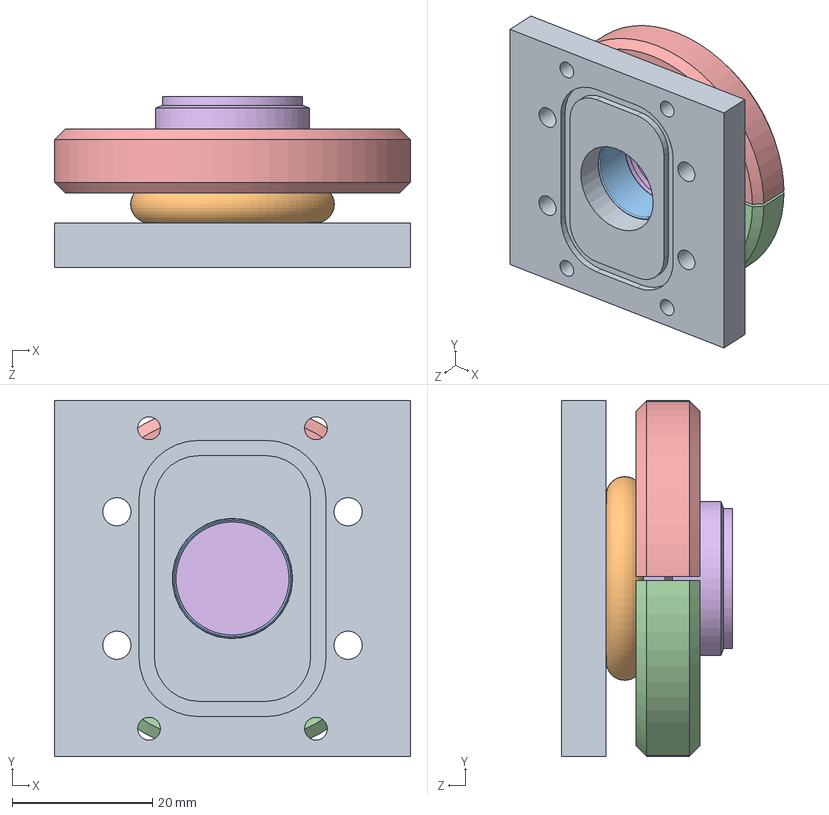
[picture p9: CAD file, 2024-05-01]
hardware/parts/other/reel_flange_qf16_feedthrough.SLDASM
50.8 x 50.8 x 24.4 mm
reel_housing_to_qf16_flange
C0001197
P0001219
QF16-075-BC-R_2
QF16-075-BC-R_3
QF16-075-VP

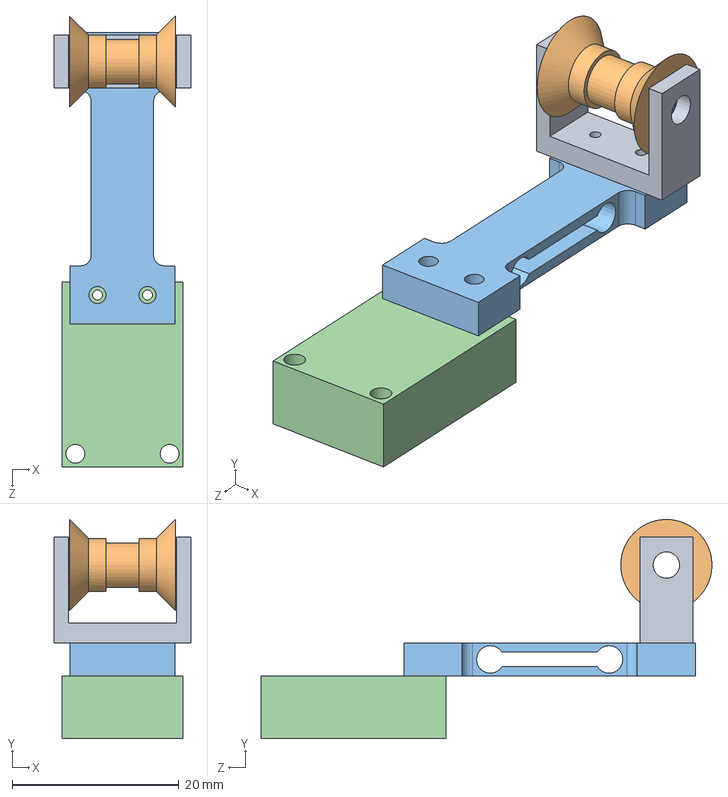
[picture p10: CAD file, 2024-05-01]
hardware/parts/tension_sensor_v2.SLDASM
16.4 x 26.3 x 54.1 mm
tension_roller_mount_v2
tension_roller_v2
100g_load_cell_RB-Phi-203
load_cell_vertical_base_v2

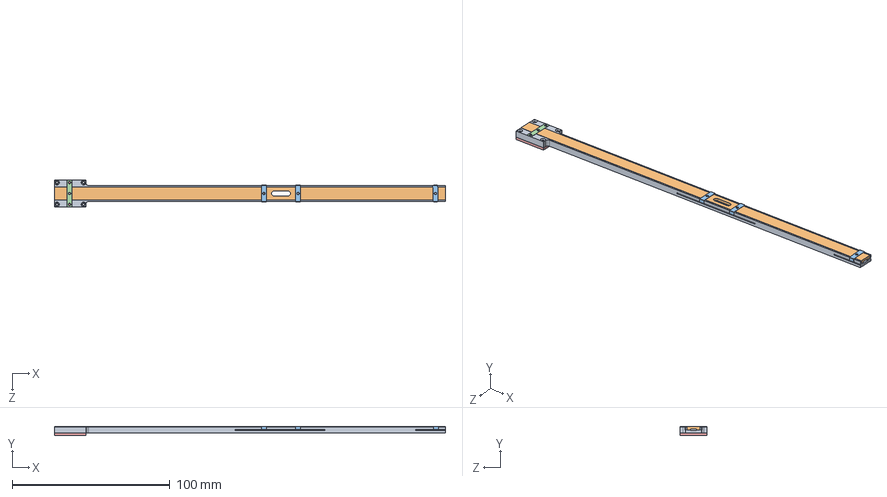
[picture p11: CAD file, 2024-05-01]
hardware/parts/other/stick_assembly.SLDASM
247.6 x 5.81 x 17.0 mm
straight_stick_v2
tape_clamp
bent_spring_clamp x 3
spring_clamp
channel_base_plate

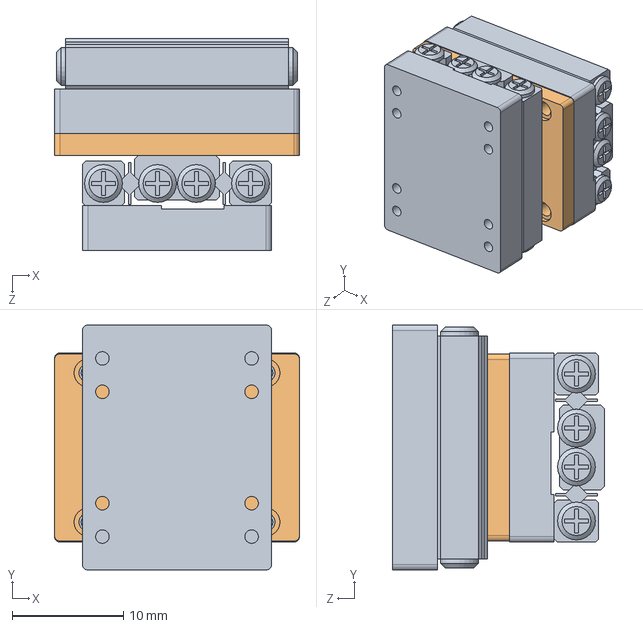
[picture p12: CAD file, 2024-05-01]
hardware/parts/other/smaract_1720s_xy.SLDASM
22.0 x 22.0 x 19.0 mm
smaract_slc1720s x 2
XY_SLC-1720-s_V2

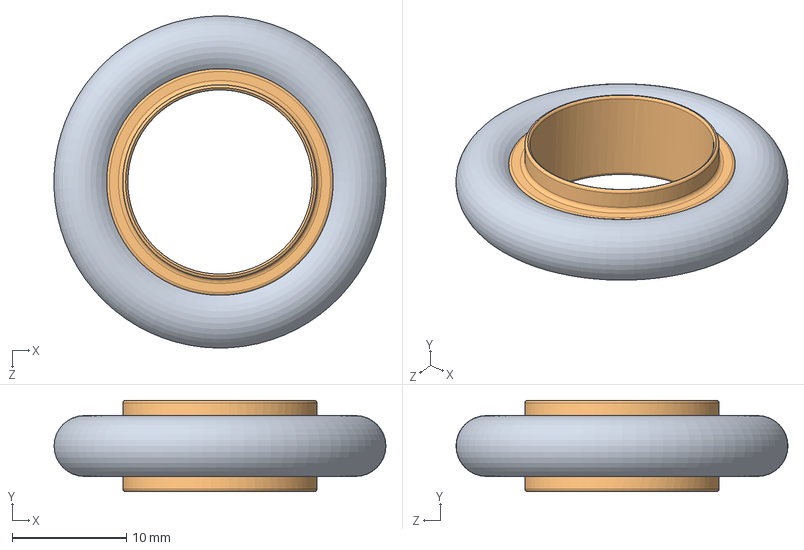
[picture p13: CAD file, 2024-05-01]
hardware/parts/other/QF16-075-ARB.sldasm
29.1 x 8.00 x 29.1 mm
C0001197
P0001219

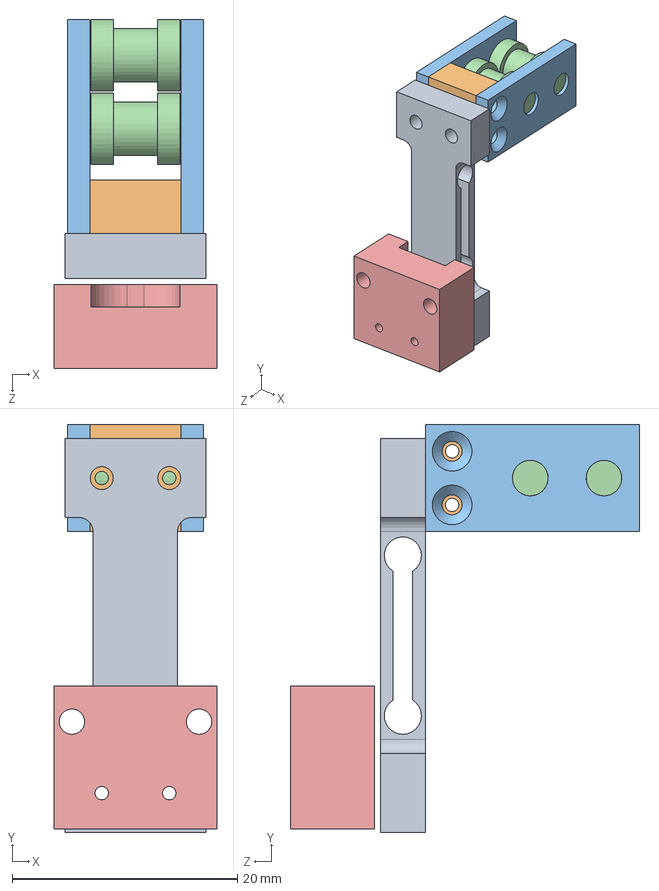
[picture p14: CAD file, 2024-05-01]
hardware/parts/other/vertical_load_cell.SLDASM
14.5 x 36.3 x 31.1 mm
100g_load_cell_RB-Phi-203
load_cell_vertical_adapter
load_cell_plate x 2
idle_roller_p25in x 2
load_cell_vertical_base

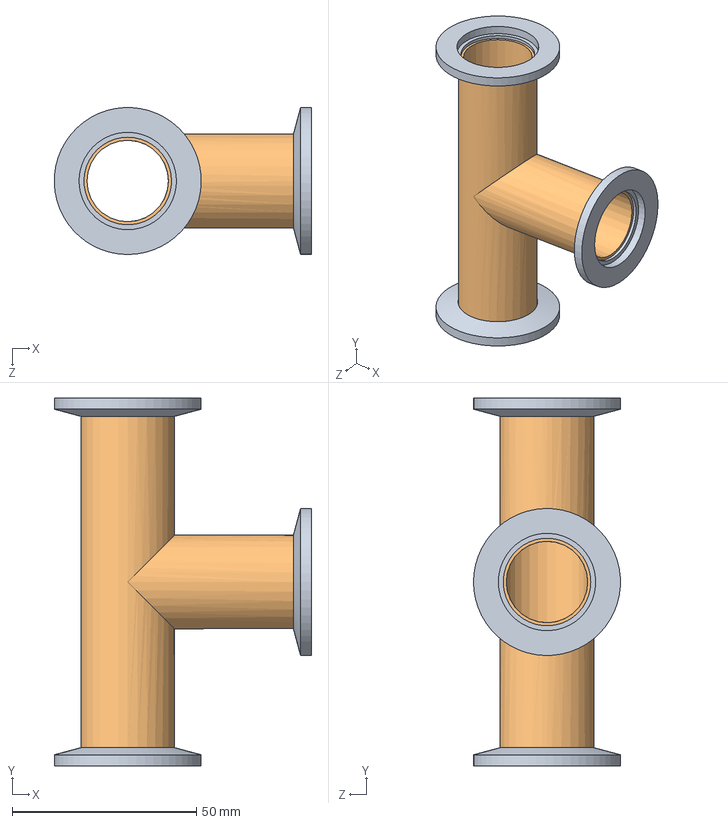
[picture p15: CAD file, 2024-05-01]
hardware/parts/other/qf25-100-t.sldasm
69.8 x 99.8 x 39.9 mm
P0001498 x 3
P0017967

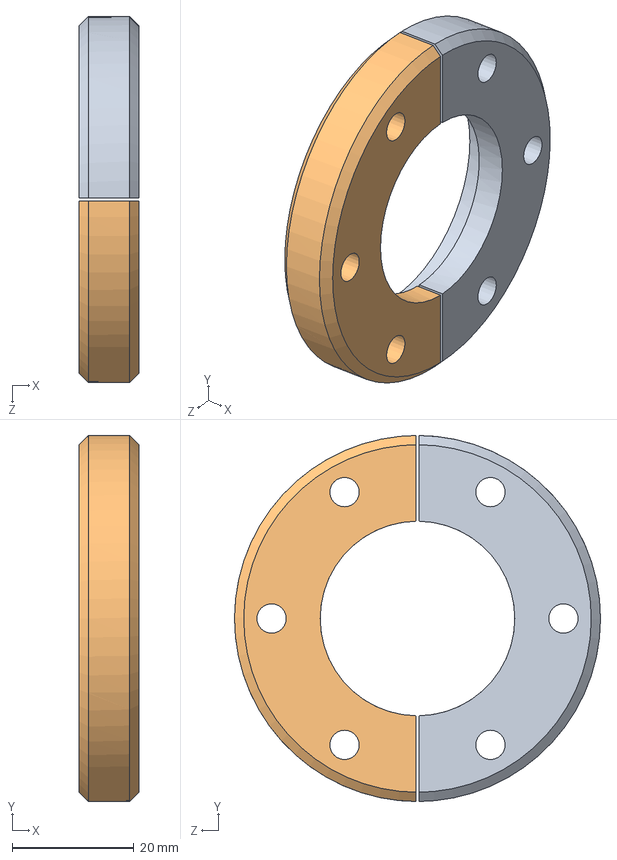
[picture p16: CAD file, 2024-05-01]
hardware/parts/other/qf25-100-bc (1).sldasm
9.83 x 60.2 x 60.2 mm

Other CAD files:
hardware/parts/other/aperture_objective.sldasm
hardware/parts/other/Ferrotec SS-188-SLEX (103073).sldasm
hardware/parts/other/JEOL 1200ex OL Module_SAP Polepiece column.sldasm
hardware/parts/other/reel.SLDASM
hardware/drawings/SI_sdpsi_s98ca6-mec160417.SLDDRW
hardware/drawings/chamber_lid_with_view.SLDDRW
hardware/drawings/chamber_v1.SLDDRW
hardware/drawings/channel_base_plate.SLDDRW
hardware/drawings/drive_roller.SLDDRW
hardware/drawings/ferrotec_clamp.SLDDRW
hardware/drawings/front_left_xy_flange.SLDDRW
hardware/drawings/load_cell_vertical_base_v2.SLDDRW
hardware/drawings/piezo_baseplate.SLDDRW
hardware/drawings/reel_adapter_screw_set_3f16.SLDDRW
hardware/drawings/reel_door.SLDDRW
hardware/drawings/reel_housing.SLDDRW
hardware/drawings/reel_housing_blank.SLDDRW
hardware/drawings/reel_housing_flange.SLDDRW
hardware/drawings/reel_housing_to_qf16_flange.SLDDRW
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

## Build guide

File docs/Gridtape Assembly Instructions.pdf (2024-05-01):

# Gridtape Assembly Instructions

(Last updated 01/11/2024)

## Custom machining notes

Piezo chamber
1. QF-25 feedthrough (smaract) and QF-25 feedthrough (tension): machine a 16.1mm bore through the center of each blank for the two lemo connectors (the “tension sensor feedthrough” and the smaract feedthrough)
2. The tension sensor roller pin is a 18-8 stainless steel dowel (not in the CAD). It can either be press fit into the roller or press fit into the side supports.

Reel housing
1. Tape roller screws (SS, 4-40 x ⅛ x ⅝ shoulder screw): cut threads with dremel to vent
3. Clean drive rollers, then glue o-rings to drive rollers (preferred vacuum compatible glue)
4. Clean the bearings and re-oil them with vacuum pump oil or vacuum grease

Motors
1. 2x pinch drive timing belt pulleys (MXL timing pulley, ⅛ wide, 15 tooth, 3/16 bore): drill out bore to 5mm (to fit over the stepper motor shafts for the pinch drive)
2. Slip clutch modifications (these are the modifications as seen on xtemgt - this slip clutch modification and assembly may be modified in the future):
a. 2x slip clutch (0.25” bore adjustable slip clutch with torque range of 0.3 to 32 OZ-IN): drill out the bore on the hub side to 0.312” in diameter and 0.224” deep (to hold the slip clutch timing belt pulley).
b. 2x slip clutch timing belt pulleys (MXL timing pulley, ⅛ wide, 18 tooth, 3/16 bore): drill out the inside bore to 0.25” in diameter. Press fit into the hub side of the slip clutch.
3. Waterjet:
a. 2x pinch_drive_clamp_short (⅛” al stock)
b. 2x reel_drive_clamp_slipclutch (⅛” al stock
4. The takeup rest is made of stainless steel, not aluminum. This is to prevent the aluminum channel from abrading away the takeup rest and permanently altering the alignment of those two components.

# Assembly

## Electronics Assembly

### Wiring Diagram

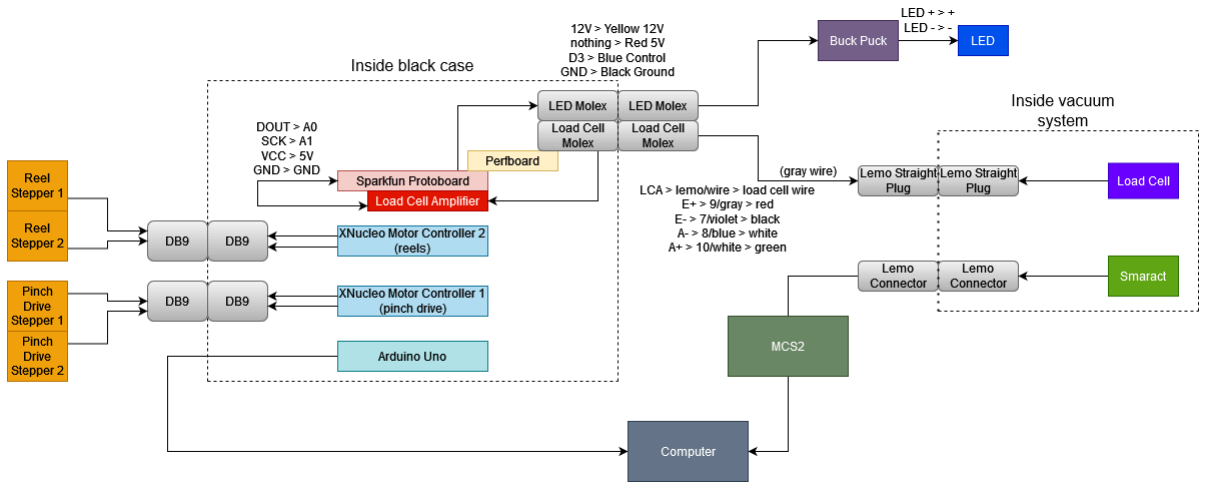
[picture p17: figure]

### Pinouts

Pins along the same row connect to one another (example of how to read a row is given for each table).

Stepper Motor pinout
(The first row reads as: the feed pinch drive stepper motor’s red wire connects to top DB-9 plug pin 1, the corresponding top DB-9 receptacle connector pin 1 connects to the top motor
controller shield ST2 2B block)
Positio n in Case | Pin Numbe r | Signa l | Stepper wire | Shiel d Input | Shield | Shield Signal | CS | Chain Index | 0 direction | Enclosure Port
Top DB-9 | 1 | Feed, Pinch | Red | ST2 | Top | 2B | A2 | 0 | CCW | Top
| 2 | Feed, Pinch | Blue | ST2 | Top | 1B | A2 | 0 | CCW | Top
| 3 | Feed, Pinch | Black | ST2 | Top | 1A | A2 | 0 | CCW | Top
| 4 | Feed, Pinch | Green | ST2 | Top | 2A | A2 | 0 | CCW | Top

| 5 | NC
| 6 | Feed, Reel | Red | ST2 | Bottom | 2B | D2 | 0 | CCW | Top
| 7 | Feed, Reel | Blue | ST2 | Bottom | 1B | D2 | 0 | CCW | Top
| 8 | Feed, Reel | Black | ST2 | Bottom | 1A | D2 | 0 | CCW | Top
| 9 | Feed, Reel | Green | ST2 | Bottom | 2A | D2 | 0 | CCW | Top
Bottom DB-9 | 1 | Picku p, Pinch | Red | ST1 | Top | 2B | A2 | 1 | CCW | Bottom
| 2 | Picku p, Pinch | Blue | ST1 | Top | 1B | A2 | 1 | CCW | Bottom
| 3 | Picku p, Pinch | Black | ST1 | Top | 1A | A2 | 1 | CCW | Bottom
| 4 | Picku p, Pinch | Green | ST1 | Top | 2A | A2 | 1 | CCW | Bottom
| 5 | NC
| 6 | Picku p, Reel | Red | ST1 | Bottom | 2B | D2 | 1 | CCW | Bottom
| 7 | Picku p, Reel | Blue | ST1 | Bottom | 1B | D2 | 1 | CCW | Bottom
| 8 | Picku p, Reel | Black | ST1 | Bottom | 1A | D2 | 1 | CCW | Bottom
| 9 | Picku p, Reel | Green | ST1 | Bottom | 2A | D2 | 1 | CCW | Bottom

LED pinout
(The first row reads as: 4-pin plug pin 1 is connected to the Arduino Vin, corresponding 4-pin receptacle pin 1 is connected to a wire that goes to Buckpuck V+)
Connector | Pin number | Signal | Buckpuck | Arduino
Right 4 pin | 1 | 12V | V+ | Vin
| 2 | 5V | REF | NOTHING
| 3 | D3 | CTL | D3
| 4 | GND | V- | GND

Load Cell pinout

(The first row reads as: 4-pin plug pin 1 connects to E+ on the load cell amplifier, corresponding 4-pin receptacle pin 1 connects to the gray cable grey wire, which connects to Lemo pin 9 (across the Lemo plug and straight connector), which connects to the load cell red wire)
Connector | Pin number | Signal | Load cell | Lemo Pin | Gray cable color
Left 4 pin | 1 | E+ | Red | 9 | Grey
(above USB) | 2 | E- | Black | 8 | Violet
| 3 | A- | White | 7 | Blue
| 4 | A+ | Green | 10 | White

### Motors

There are two motor controller boards (X-NUCLEO-IHM02A1) on the GridTape system. Each can drive two stepper motors. The two pinch drive motors will connect to one controller. The two reel motors will connect to the second controller. The controllers will need to be modified to make them Arduino compatible, but they can physically mount onto an Arduinio Uno board out of the box.

Do note that there is bare bones documentation for Arduino compatibility and one small github library for the Arduino Uno API. The boards are VOLTAGE controlled, not current controlled.

On both boards:
- Unsolder SB40, solder SB41
- Unsolder SB34, solder SB12
On the reel board:
Unsolder SB23, solder SB7

For the boards, the feed side motors always connect to ST2 (see the marking on the x-nucleo board) and the pickup side motors always connect to ST1 (also see the x-nucleo board).

Solder the feed steppers to a single DB9 and the pickup steppers to a single DB9, as shown below (and detailed above):

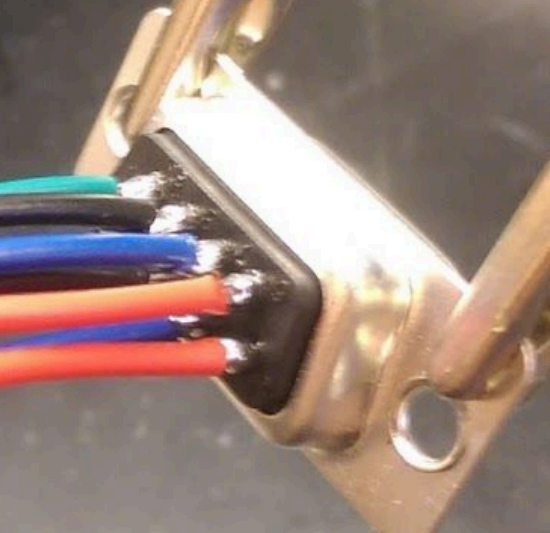
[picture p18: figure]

Solder the corresponding DB9’s connectors to wires that screw into the terminal blocks of the motor controller boards.

The feed side motor controller stacks on top of the pickup side motor controller, and both then stack on top of the Arduino Uno.

### Sparkfun Protoshield to load cell and LED connectors

Cut a 14 hole x 14 hole piece of protoboard and solder it to the edge of a Sparkfun protoshield so that 6 rows of holes hang off the edge on the side of the protoshield that lines up with the USB edge of the Arduino. Solder two 4-pin right angle molex connectors to the far edge of the protoboard. This is so the molex connectors can protrude from the sides of the black case.

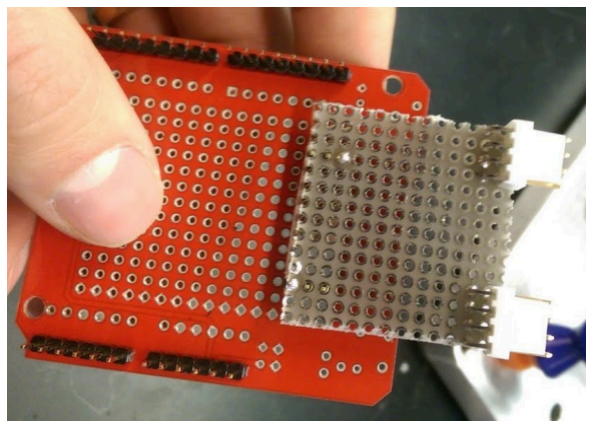
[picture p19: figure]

Any 4-pin connector should work, image uses JST connectors

Place the load cell amplifier on the bottom face of the Sparkfun protoshield and solder jumper wires to connect the Arduino, load cell amplifier and the 2x 4 pin connectors. The connectors will be used for the load cell (tension sensor) and LED.

### Load cell connector

Consult the table above for the pinout.

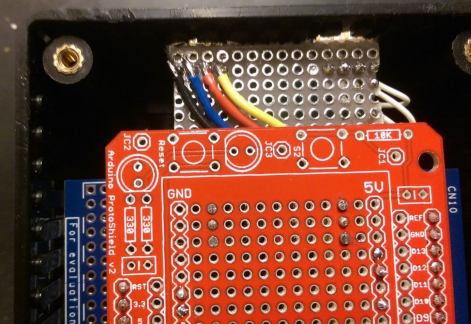
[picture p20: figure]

The Sparkfun protoshield with attached load cell amplifier and protoboard stack on top of the motor controller boards.

Load cell cabling with Lemo connectors
Use kapton insulated wire and silver solder (for vacuum compatibility reasons) to extend the tension sensor’s four wires by about 6in to fit through the T junction. Connect these wires to the Lemo plug (shown below) like so (Load Cell pinout table also shows these connections across the whole load cell path):
- Load cell Red > Plug 9
- Load cell Black > Plug 8
- Load cell White > Plug 7
- Load Cell Green >Plug 10

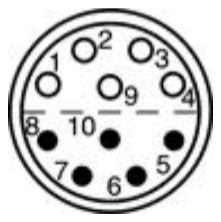
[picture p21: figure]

Lemo plug from the back:
- https://www.mouser.com/datasheet/2/232/HGP_2S_310_CLLPV-1941806.pdf
- Load cell extended wires connect here!
- Dark holes correspond to protruding pins, light holes correspond to enclosed pins

The load cell lemo plug connects to the load cell amplifier via a gray connector cable. The connector cable is composed of a stripped end crimped into a molex connector and a stripped end soldered into a lemo straight connector. The straight lemo connector must be partially disassembled to reach the pins in the back. This cable-lemo join requires an order of operations
- take the back screw + spring tensioner off of the lemo straight connector and loop them onto the cable end that you’re going to solder to FIRST. Then strip the wires and solder to the back of the connector. And then assemble. Otherwise you will be sad. The gray connector cable is soldered to the lemo straight connector like so (Load Cell pinout table also shows these connections across the whole load cell path):
- Cable Gray > Straight connector 9
- Cable Violet > Straight connector 8
- Cable Blue > Straight connector 7
- Cable White > Straight connector 10

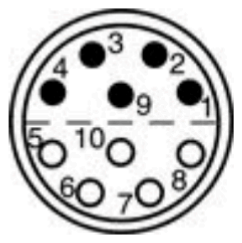
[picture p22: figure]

Lemo straight connector from the back
- Gray connector cable goes here!
- Dark holes correspond to protruding pins, light holes correspond to enclosed pins

The gray connector cable is then stripped and the four wires that lead to the load cell amplifier crimped into a molex connector.

### LED

Solder jumper wires from the Sparkfun protoshield Vin, D3, and GND to the remaining molex connector . This connector will go to the LED. Consult the table above for the pinout.

Make a 1.5ft yellow, red, blue, black wire bundle. Crimp one end of the wires into a 4 pin molex connector so that it lines up with the molex connector on the protoboard. Crimp the other end of the wires into a 4 pin header socket to attach to the buck puck. Connect the LED- and GND on the buck puck and solder the LED+ and LED- to the LED.

Tap 4-40 holes into a heatsink and lightly fix the LED to the heatsink with some thermal tape. Screw the LED into the heatsink. Double sided tape the buckpuck to the other side of the heat sink and zip tie the heat sink to the LED mount.

### Enclosure

Cut access holes on both small faces of the black plastic case.
- Face 1:
- Arduino USB
- Two molex connectors
- Face 2:
- Power plug
- Two DB9 connectors

Something like the following template (scaled to fit the ends of the enclosure)

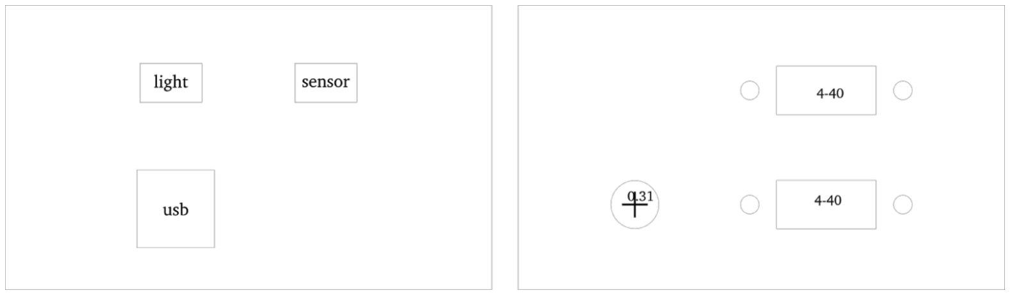
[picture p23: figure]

## Hardware

### Deburr parts and make final modifications

1. Channel (top/bottom):
a. Deburr and polish channel surfaces
b. Round off channel entrance and exit
2. Make sure piezo plates are flat and burr free
3. Check all oring sealing surfaces

### Chamber cleaning

Clean all parts that will go into vacuum with the following:
1. Wipe off any visible dirt
2. Wash in hot water and alconox
3. If possible, place in ultrasonic cleaner for 5 minutes with alconox and water
4. Rinse thoroughly with hot water
5. Rinse with DI water
6. Rinse with Acetone
7. Rinse with 100% ethanol

FIrst assembly! Do follow this in order, the order is kind of important to avoid blocking screws.
1. Piezo chamber
a. Take the piezo-to-column-flange (front_left_xy_flange) and slip a Viton75-027 o-ring onto the scope insert end and place a Viton75-027 on the flat piezo chamber-side face. Attach the front_left_xy_flange to the column with 4 SS M6x10mm SHCS low profile.
b. Attach the piezo chamber (chamber_v1) to the piezo-to-column-flange with 4 SS M5x16mm SHCS.
c. Attach the Smaract piezo stack to the piezo base plate (piezo_baseplate) with 4 M1.6x4mm FH. Attach the piezo base plate to the bottom of the piezo chamber with 4 SS 2-56x3/16 SHCS vented.
d. Attach the right side of the T in the Lesker KF25 T junction to the side of the piezo chamber with Lesker QF25 Al clamps and Lesker KF25 centering silicone o-ring.
e. Feed the Lemo feedthrough attached to the Smaract piezo stack through one free arm of the Lesker KF25 T junction.
f. Attach the load cell mounting block (load_cell_vertical_base_v2) to the piezo chamber with 2 SS 2-56x3/8 SHCS vented.
g. Unscrew the nut at the Lemo connector attached to the load cell. Feed the load cell through the KF25 flange, then through the nut, then through the remaining free arm of the Lesker KF25 T junction into the piezo chamber. Attach the tension roller (tension_roller_mount, tension_roller_v2) on top of the wire-free end of the load cell with 2 SS 0-80x1/4 FH. Attach the wire-end of the load cell on top of the load cell mounting block with 2 SS 0-80x1/4 FH.
h. Place a KF25 centering silicone o-ring on each free end of the Lesker KF25 T junction. Take the connector pair of the Smaract Lemo connector and connect the two through a machined KF25 flange (make sure the furrowed face is facing the T junction opening). Take the connector pair of the load cell Lemo connector and connect the two through a second machined KF25 flange (make sure the furrowed face is facing the T junction opening). Put each KF25 flange on the KF25 centering silicone o-ring and clamp each in place with a KF25 wingnut clamp.
i. Place a KF16 centering silicone o-ring on the opening in the flat (no gland) face of the piezo chamber lid (chamber_lid_with_view) and place a KF16 viewport on top of the o-ring. Secure it all down with a KF16 bulkhead clamp. Place a Viton75-036 o-ring in the lid gland and screw it down on top of the piezo chamber with 4 SS 6-32x1/2 FHSC.
2. Channel and Scope
a. Add Viton 75-122 o-rings to the takeup rest (takeup_rest_insert). Insert it into the right opening of the scope so that the flat side of the through-hole is on the bottom.
b. Spread a very fine layer of vacuum grease on the lower surface of the bore in the takeup rest.
c. Tape the channel, ensuring that a doubled up piece of gridtape will slide through the channel with ~15g of force, and insert through the piezo chamber until the end of the channel rests on top of the takeup rest.
d. Add a Viton 75-219 o-ring to the gland side of the takeup_reel_flange, and attach it to the scope with 2 SS M4x10mm FHSC, so that the screws are on the top half of the flange and the o-ring is pressed flat against the scope.
3. Feed and Pickup Reel housing (instructions for one housing)
a. Insert the Ferrotec feedthroughs for the pinch drive and the reel motor. DO NOT fix them in place yet.
b. Slide the inner spacer (inner_spacer) into the center of the idle roller (roller). Place a ⅛ shaft ¼ flanged bearing on either side of the through-hole in the idle roller. Slide a SS 4-40x1/8 x ⅝ shoulder screw through the bearings. The roller spacer (roller_spacer) should be slid onto the thread end of the shoulder screw -this is so the idle roller is positioned correctly when the shoulder screw is screwed into the housing. .
c. Place the active roller (drive_roller) and the idle roller in contact so that the o-rings on the active roller fit inside the outermost flanges of the idle roller. With the active roller and the idle roller together, slide the active roller onto the upper Ferrotec feedthrough shaft inside of the reel housing and screw in the shoulder screw into the threaded hole closest to the scope. Make sure to keep the roller as in-line with one another as possible. Mount the active roller on the feedthrough shaft with 2 SS 8-32x1/4 set screw vented.
d. Mount the reel hub (reel_adapter_screw_set_3f16) onto the lower Ferrotec feedthrough shaft inside of the reel housing with SS 8-32x1/4 set screw vented. Make sure that the reel hub is aligned with the pinch drive.
e. Add a Viton 75-027 o-ring to the reel face of the reel flange (reel_housing_flange) and secure it to the reel housing with 4 4-40x3/8 FHSC.
f. Add a Viton 75-027 o-ring to the QF16 reel flange (reel_housing_to_qf16_flange) and secure it onto the open window (the one facing away from the scope) in the side of the reel housing with 4 4-40x3/8 FHSC screws. Place the KF16 centering silicone o-ring onto the opening in the flange, set the KF16 viewport on the centering silicone o-ring, and then secure it down with a KF16 bulkhead clamp.
g. And split depending on feed/pickup reel:
i. Feed reel: Add pinch drive motor mount (pinch_drive_clamp_short) and reel motor mounts (reel_drive_clamp_slipclutch) with 6 SS 4-40x3/8 SHCS. Add the upper left screw (SS 6-32x7/16 FHSC)from the reel housing flange into the piezo chamber and then fix the Ferrotec feedthroughs in place with the Ferrotec clamps (ferrotec_clamp) and 4 SS 2-56x5/16 FHSC each. Finish attaching the reel housing flange to the piezo chamber with 3 SS 6-32x7/16 FHSC.
ii. | Pickup reel: Attach reel housing flange (reel_housing_flange) to takeup
| reel flange (takeup_reel_flange) with 4 SS 6-32x7/16 FHSC. Add the
| pinch drive motor mount (pinch_drive_clamp_short) and reel motor
| mounts (reel_drive_clamp_slipclutch) with 6 SS 4-40x3/8 SHCS. Fix the
| Ferrotec feedthroughs in place with the Ferrotec clamps (ferrotec_clamp)
| and 4 SS 2-56x5/16 FHSC each.
h. Mount the pulleys on the Ferrotec feedthroughs. Loop the corresponding belts over the pulleys.
i. Mount the reel motor shaft adaptor (shaft_adapter_slipclutch) to the reel drive motors, mount the pulley onto the slipclutch, then mount the slipclutch onto the shaft adaptor.
j. Mount the motors onto the pinch drive motor mounts and reel motor mounts. Make sure to loop the belt around the motor pulley and to give some tension on the belt when screwing in the motors with 16 SS M2.5x6mm BHSC.

## Testing

### Vacuum Testing (off scope)

Vacuum test the following:
- Reel housings (feed and pickup)
- With no extra flanges

- WIth all extra flanges
- Piezo chamber
- Alone
- With KF-25 Tee
- With reel housings

### Movement testing

Test that piezos move with no reported errors Test pinch drive movements and note directions Test tape movement

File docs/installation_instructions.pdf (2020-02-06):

Revision 161021

# Stage part removal and reinstallation

## Reel housing door

The reel housing door is affixed to the reel housing body by 10x #4-40 screws. To remove the door, first slightly loosen all screws (following a staggered or criss crossed pattern). Then, with care not to drop the door, remove the screws and be sure not to drop the door or sealing oring (dash 048).

Installation follows the steps in reverse. First be sure the oring is seated in the gland, carefully place the door against the housing making sure the oring stays seated. Insert and lightly screw in all screws, then tighten all screws (following a staggered pattern).

## Feed reel housing

Removal of the feed reel housing involves the following steps:
1. Remove the feed reel housing door to gain access to the #6-32 reel housing flange screws
2. While supporting the reel housing, remove the reel housing flange screws (A, B, C, D) below

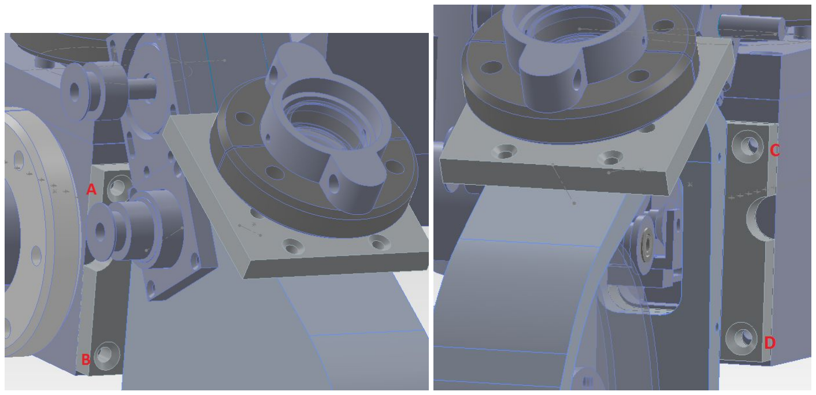
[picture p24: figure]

Installation follows the steps in reverse. Be sure to tighten screws in a staggered pattern.

## Pickup reel housing

Removal of the pickup reel housing involves the following steps.

1. Remove the pickup reel housing door to gain easier access to the M4 pickup housing mounting screws, A and B below
2. Access to B requires a very long allen key that was included with the stage
3. Be sure the pickup reel housing is supported and loosen then remove both A and B

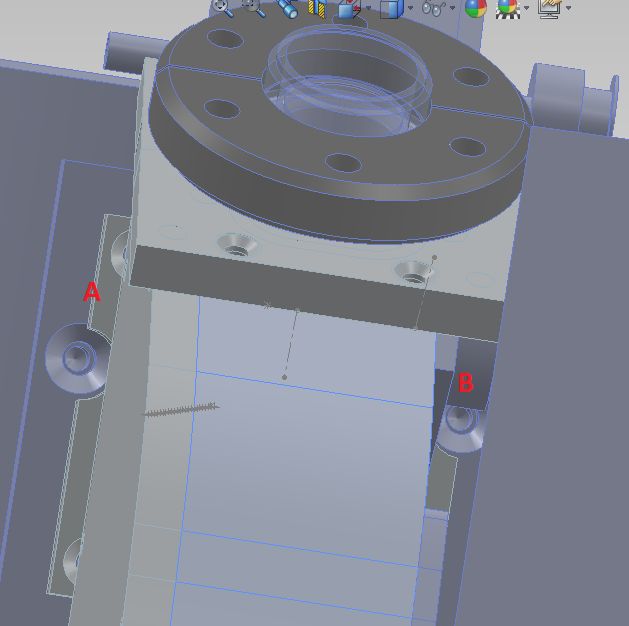
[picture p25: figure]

Installation follows the steps in reverse. It is often easier to start by starting to thread in screw B, then while continuing to support the reel housing, start screw A, then snug both screws, then tighten them (while tightening B it is normal for the allen key to twist given the extended length).

## Piezo chamber lid

To remove the piezo chamber lid, remove the #10-32 screws ABCD below.

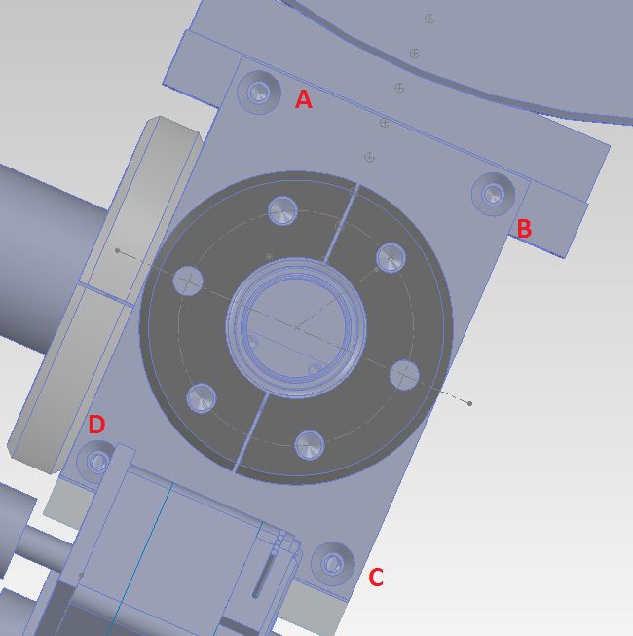
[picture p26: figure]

Screw D can be unthreaded but cannot be removed until the piezo chamber lid is slid to the right.
While sliding the chamber lid make sure that the oring (dash 036) does not fall out of the gland.

Installation follows the steps in reverse, First, insert screw D into the lid, then slide it into place from the right, then tighten all screws in a staggered order.

## Tape channel

Removal of the tape channel involves the following steps
1. Remove the feed reel housing
2. Remove the piezo chamber lid
3. Remove the #0-80 screws A-D below
4. Taking care that the channel slides along the piezo stack, and does not pitch significantly (which can result in the channel contacting the pole piece or other parts of the scope), slide the channel out of the piezo chamber through the hole where the feed reel housing was mounted (bottom of the image below).

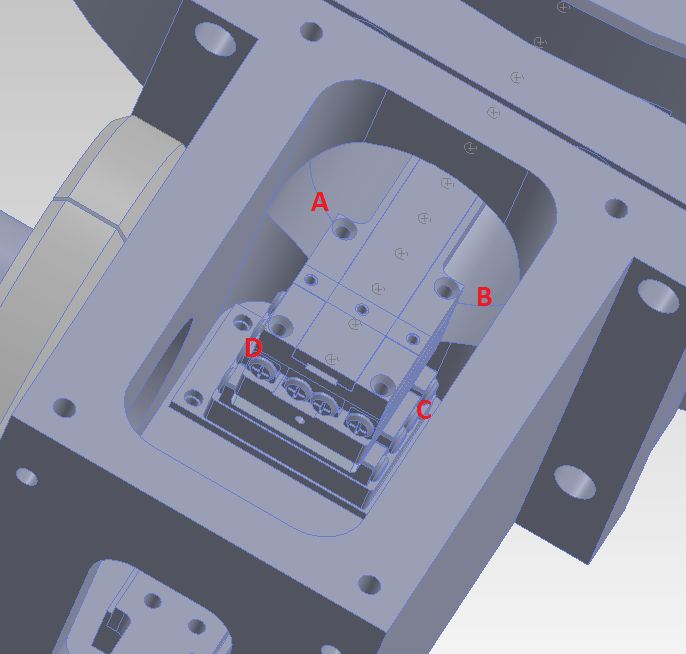
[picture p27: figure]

To disassemble the channel, remove the pieces of copper tape affixing the channel clamp to the channel body. To reassemble the channel, take 2x pieces of 125 um 8 mm wide Kapton film (no adhesive). Sandwich both pieces between the channel clamp and body. Press down on the sandwich while reapplying fresh copper tape. Remove the 2x pieces of Kapton film and test that the channel has the appropriate clamping force. The clamping force can be tested by attaching a weight (for example 30 grams) to a single piece of 125 um Kapton film (no adhesive), feeding the film through the channel, holding the channel vertically, and checking that the tape does not slide until additional weight is added.

Installation of the channel involves the following steps.
1. Remove the pickup reel housing
2. Remove the feed reel housing
3. Remove the piezo chamber lid
4. Slide the channel through the opening in the piezo chamber where the feed reel housing is usually attached (see the removal step #4 above) into the microscope and verify that the end of the channel is lightly resting on the pickup rest (see the image below).
5. Affix the channel to the piezo stack (see removal step #3)
6. Verify the piezo stack can move the channel in both X and Y
7. Reattach the pickup reel housing
8. Reattach the feed reel housing
9. Reattach the piezo chamber lid

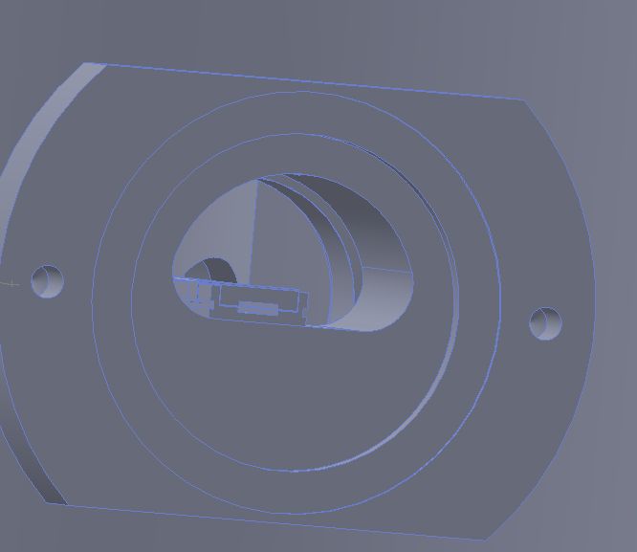
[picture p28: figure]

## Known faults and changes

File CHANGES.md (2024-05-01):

# Dec 2023 - [Updating CAD and BOM to reflect slip clutch changes](https://github.com/htem/GridTapeStage/pull/3)
## Hardware
### Parts
- Updated the reel_drive_clamp and shaft_adapter CAD to their slip clutch varients
- Added slip clutch and slip clutch pulley CAD 
- Updated overall CAD assembly to include slip clutch and slip clutch adjacent CAD
- Added missing counterbore to back of `reel_adapter'
### Drawings
	- Added drawings of updated CAD

## Docs
### BOM
- Changed the reel drive plate and slip clutch shaft CAD file reference to reel_drive_clamp_slipclutch and shaft_adatper_slipclutch
- Removed components for old slipclutch
- Added current slipclutch
- Changed the material of the takeup_rest from aluminum to stainless steel
- Included 4-pin connectors for the load cell amplifier and the LED, and a 7pos housing receptacle for the LED buckpuck
### Assembly Instructions

details about the assembly instructions changes...

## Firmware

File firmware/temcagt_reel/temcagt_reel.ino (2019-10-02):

/*
 * Temcagt reel control
 * 2015/11/16 : Brett Graham
 *
 * One arduino to control the reel-to-reel mechanism including
 * - tension measurement (HX711)
 * - 2x pinch drive control (dSPIN)
 * - 2x reel drive control (dSPIN)
 *
 * Make this just as 'dumb' as possible
 *
 * Dumbest is:
 * - read tension
 * - move pinch drive [i] by [x]
 * - rotate reel drive [i] at [rpm]
 * - set led
 *
 * A little smarter is
 * - {all above}
 * - set tension low limit [v]
 * - set tension limit high [v]
 * - move pinch drives by [x] watching tension
 * - read moved distance (from eeprom)
 * - write moved distance (to eeprom)
 */

#include <comando.h>
#include "HX711.h"
#include <SPI.h>
#include <dSPIN.h>

#define RUN_KV_PINCH 128
#define RUN_KV_REEL 64
#define RUN_KV 64
#define HOLD_KV 16

#define PINCH_MM_PER_USTEP 0.002734375
#define REEL_MM_PER_REV 120.0

// reel motor 2xdspin board chip select
#define R_SELECT 2
// pinch motor 2xdspin board chip select
#define P_SELECT A2
#define MOSI 11
#define MISO 12
#define SCK 13
#define RESET 4
#define BUSY A5
#define FLAG A4

#define SCALE_DOUT A0
#define SCALE_SCK A1

#define LED 3

// numbered with 0 at the END of the chain, so ST2 = 0, ST1 = 1
#define PICKUP 1
#define FEED 0

#define COLLECT 0
#define DISPENSE 1
#define TENSION 2
#define UNTENSION 3

#define FEED_REEL    B00000000
#define FEED_PINCH   B00000001
#define PICKUP_REEL  B00000010
#define PICKUP_PINCH B00000011

#define CMD_ERROR 0  // -> error_code [byte]
#define CMD_PING 1 // (value [byte]) -> (value [byte])

#define CMD_READ_TENSION 5  // (n_samples [byte]) -> tension [long]
#define CMD_SET_LED 6  // value [byte]

#define CMD_RESET_DRIVES 10
#define CMD_GET_BUSY 11  // (drive [byte]) -> busy [byte]
#define CMD_GET_STATUS 12  // drive [byte] -> status [int]
#define CMD_GET_POSITION 13  // drive [byte] -> position [long]
#define CMD_SET_POSITION 14  // drive [byte], position [long]
#define CMD_HOLD_DRIVE 15  // drive [byte]
#define CMD_RELEASE_DRIVE 16 // drive [byte]
#define CMD_ROTATE_DRIVE 17  // drive [byte], dir [byte], speed [float]
#define CMD_SET_SPEED 18  // drive [byte], speed [float]
#define CMD_GET_SPEED 19  // drive [byte] -> speed [float]
#define CMD_MOVE_DRIVE 20  // drive [byte], dir [byte], n_steps [ulong]

#define CMD_RUN_REELS 21
#define CMD_STOP_REELS 22
#define CMD_STOP_ALL 23
#define CMD_RELEASE_ALL 24
#define CMD_HALT_ALL 25

// dir [byte], f_steps [ulong], p_steps [ulong], time [float], opts [byte] -> []
#define CMD_STEP_TAPE 30
// low [long], high [long]
#define CMD_SET_TENSION_LIMITS 31
// -> low [long], high [long]
#define CMD_GET_TENSION_LIMITS 32

#define ST_OPTS_RUN_REELS 0x01
#define ST_OPTS_WAIT 0x02
#define ST_OPTS_WATCH 0x04

#define ERR_ERROR 0
#define ERR_INVALID_CMD 1
#define ERR_MISSING_ARG 1
#define ERR_INVALID_ARG 2
#define ERR_INVALID_DRIVE 10
#define ERR_INVALID_DIRECTION 11
#define ERR_TENSION 20

// comando
Comando com = Comando(Serial);
EchoProtocol echo = EchoProtocol(com);
CommandProtocol cmd = CommandProtocol(com);

// scale
long tension_low_limit = 8460000;
long tension_high_limit = 8470000;
HX711 scale(SCALE_DOUT, SCALE_SCK);

// reel and pinch motors
dSPIN reels(R_SELECT, RESET, BUSY);
dSPIN pinches(P_SELECT, RESET, BUSY);


void setup() {
  // setup led pin
  pinMode(LED, OUTPUT);
  led_off();
  
  // connect to Serial
  Serial.begin(115200);
  com.register_protocol(0, echo);
  com.register_protocol(1, cmd);
  
  // connect to dspin boards [4]
  configure_drives();
  
  // connect to hx711
 
  // register callbacks
  cmd.register_callback(CMD_PING, ping);
  
  cmd.register_callback(CMD_READ_TENSION, read_tension);
  cmd.register_callback(CMD_SET_LED, set_led);

  cmd.register_callback(CMD_RESET_DRIVES, reset_drives);
  cmd.register_callback(CMD_GET_BUSY, get_busy);
  cmd.register_callback(CMD_GET_STATUS, get_status);
  cmd.register_callback(CMD_GET_POSITION, get_position);
  cmd.register_callback(CMD_SET_POSITION, set_position);
  cmd.register_callback(CMD_HOLD_DRIVE, hold_drive);
  cmd.register_callback(CMD_RELEASE_DRIVE, release_drive);
  cmd.register_callback(CMD_ROTATE_DRIVE, rotate_drive);
  cmd.register_callback(CMD_SET_SPEED, set_speed);
  cmd.register_callback(CMD_GET_SPEED, get_speed);
  cmd.register_callback(CMD_MOVE_DRIVE, move_drive);

  cmd.register_callback(CMD_RUN_REELS, run_reels);
  cmd.register_callback(CMD_STOP_REELS, stop_reels);
  cmd.register_callback(CMD_STOP_ALL, stop_all);
  cmd.register_callback(CMD_RELEASE_ALL, release_all);
  cmd.register_callback(CMD_HALT_ALL, halt_all);
  
  cmd.register_callback(CMD_STEP_TAPE, step_tape);
  cmd.register_callback(CMD_SET_TENSION_LIMITS, set_tension_limits);
  cmd.register_callback(CMD_GET_TENSION_LIMITS, get_tension_limits);
}


void loop() {
  com.handle_stream();
}

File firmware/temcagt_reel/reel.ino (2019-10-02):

void ping(CommandProtocol *cmd) {
  byte v = 0;
  if (cmd->has_arg()) {
    v = cmd->get_arg<byte>();
  }
  cmd->start_command(CMD_PING);
  cmd->add_arg(v);
  cmd->finish_command();
}

void error(byte code) {
  cmd.start_command(CMD_ERROR);
  cmd.add_arg(code);
  cmd.finish_command();
}

void error() {
  error(ERR_ERROR);
}

void configure_drive(dSPIN drive) {
  drive.resetDev();
  drive.configSyncPin(BUSY, 0);
  drive.configStepMode(STEP_FS_128);
  drive.setMaxSpeed(1024);
  drive.setFullSpeed(10000);
  drive.setAcc(16);
  drive.setDec(512);
  drive.setSlewRate(SR_530V_us);
  drive.setOCThreshold(OC_1125mA);
  drive.setPWMFreq(PWM_DIV_2, PWM_MUL_2);
  drive.setOCShutdown(OC_SD_DISABLE);
  drive.setSwitchMode(SW_USER);
  drive.setOscMode(INT_16MHZ_OSCOUT_16MHZ);
  drive.setAccKVAL(RUN_KV);
  drive.setDecKVAL(RUN_KV);
  drive.setRunKVAL(RUN_KV);
  drive.setHoldKVAL(HOLD_KV);
  drive.setLoSpdOpt(true);
  drive.setVoltageComp(VS_COMP_DISABLE);
}

void configure_reel_drive(dSPIN drive) {
  configure_drive(drive);
  drive.setStallThreshold(15);  // empirical
  drive.setOCThreshold(OC_1125mA);
  drive.setOCShutdown(OC_SD_DISABLE);
  drive.setAccKVAL(RUN_KV_REEL);
  drive.setDecKVAL(RUN_KV_REEL);
  drive.setRunKVAL(RUN_KV_REEL);
  drive.setHoldKVAL(HOLD_KV);
  drive.setAcc(512);
  drive.setDec(512);
}

void configure_pinch_drive(dSPIN drive) {
  configure_drive(drive);
  drive.setStallThreshold(15);  // empirical
  drive.setOCThreshold(OC_1125mA);
  drive.setOCShutdown(OC_SD_DISABLE);
  drive.setAccKVAL(RUN_KV_PINCH);
  drive.setDecKVAL(RUN_KV_PINCH);
  drive.setRunKVAL(RUN_KV_PINCH);
  drive.setHoldKVAL(HOLD_KV);
}

void configure_drives() {
  configure_reel_drive(reels);
  configure_pinch_drive(pinches);
}

void reset_drives() {
  configure_drives();
}

void reset_drives(CommandProtocol *cmd) {
  reset_drives();
}

void get_busy(CommandProtocol *cmd) {
  byte r;
  if (cmd->has_arg()) {
    byte drive = cmd->get_arg<byte>();
    switch (drive) {
      case FEED_REEL:
        r = reels.getBusy(FEED);
        break;
      case FEED_PINCH:
        r = pinches.getBusy(FEED);
        break;
      case PICKUP_REEL:
        r = reels.getBusy(PICKUP);
        break;
      case PICKUP_PINCH:
        r = pinches.getBusy(PICKUP);
        break;
      default:
        error(ERR_INVALID_DRIVE);
        r -= 1;
    }
  } else {
    if (digitalRead(BUSY) == HIGH) {
      r = 0;
    } else {
      r = 1;
    }
  }
  // all busy pins are connected
  cmd->start_command(CMD_GET_BUSY);
  cmd->add_arg(r);
  cmd->finish_command();
}

void get_status(CommandProtocol *cmd) {
  if (!cmd->has_arg()) {
    error(ERR_MISSING_ARG);
    return;
  }
  // check type, check side
  int r = 0;
  switch (cmd->get_arg<byte>()) {
    case FEED_REEL:
      r = reels.getStatus(FEED);
      break;
    case FEED_PINCH:
      r = pinches.getStatus(FEED);
      break;
    case PICKUP_REEL:
      r = reels.getStatus(PICKUP);
      break;
    case PICKUP_PINCH:
      r = pinches.getStatus(PICKUP);
      break;
    default:
      error(ERR_INVALID_DRIVE);
      r -= 1;
  }
  cmd->start_command(CMD_GET_STATUS);
  cmd->add_arg(r);
  cmd->finish_command();
}

void get_position(CommandProtocol *cmd) {
  if (!cmd->has_arg()) {
    error(ERR_MISSING_ARG);
    return;
  }
  // check type, check side
  long r = 0;
  switch (cmd->get_arg<byte>()) {
    case FEED_REEL:
      r = reels.getPos(FEED);
      break;
    case FEED_PINCH:
      r = pinches.getPos(FEED);
      break;
    case PICKUP_REEL:
      r = reels.getPos(PICKUP);
      break;
    case PICKUP_PINCH:
      r = pinches.getPos(PICKUP);
      break;
    default:
      error(ERR_INVALID_DRIVE);
      r -= 1;
  }
  cmd->start_command(CMD_GET_POSITION);
  cmd->add_arg(r);
  cmd->finish_command();
}

void set_position(CommandProtocol *cmd) {
  if (!cmd->has_arg()) {
    error(ERR_MISSING_ARG);
    return;
  }
  // check type, check side
  byte drive = cmd->get_arg<byte>();
  if (!cmd->has_arg()) {
    error(ERR_MISSING_ARG);
    return;
  }
  long pos = cmd->get_arg<long>();
  switch (drive) {
    case FEED_REEL:
      reels.setPos(pos, FEED);
      break;
    case FEED_PINCH:
      pinches.setPos(pos, FEED);
      break;
    case PICKUP_REEL:
      reels.setPos(pos, PICKUP);
      break;
    case PICKUP_PINCH:
      pinches.setPos(pos, PICKUP);
      break;
    default:
      error(ERR_INVALID_DRIVE);
  }
}

void hold_drive(CommandProtocol *cmd) {
  if (!cmd->has_arg()) {
    error(ERR_MISSING_ARG);
    return;
  }
  // check type, check side
  byte drive = cmd->get_arg<byte>();
  switch (drive) {
    case FEED_REEL:
      reels.softStop(FEED);
      break;
    case FEED_PINCH:
      pinches.softStop(FEED);
      break;
    case PICKUP_REEL:
      reels.softStop(PICKUP);
      break;
    case PICKUP_PINCH:
      pinches.softStop(PICKUP);
      break;
    default:
      error(ERR_INVALID_DRIVE);
  }
}

void release_drive(CommandProtocol *cmd) {
  if (!cmd->has_arg()) {
    error(ERR_MISSING_ARG);
    return;
  }
  // check type, check side
  byte drive = cmd->get_arg<byte>();
  switch (drive) {
    case FEED_REEL:
      reels.softHiZ(FEED);
      break;
    case FEED_PINCH:
      pinches.softHiZ(FEED);
      break;
    case PICKUP_REEL:
      reels.softHiZ(PICKUP);
      break;
    case PICKUP_PINCH:
      pinches.softHiZ(PICKUP);
      break;
    default:
      error(ERR_INVALID_DRIVE);
  }
}

void rotate_drive(CommandProtocol *cmd) {
  if (!cmd->has_arg()) {
    error(ERR_MISSING_ARG);
    return;
  }
  // check type, check side
  byte drive = cmd->get_arg<byte>();
  if (!cmd->has_arg()) {
    error(ERR_MISSING_ARG);
    return;
  }
  byte dir = cmd->get_arg<byte>();
  if ((dir != 0) && (dir != 1)) {
    error(ERR_INVALID_ARG);
    return;
  }
  if (!cmd->has_arg()) {
    error(ERR_MISSING_ARG);
    return;
  }
  float speed = cmd->get_arg<float>();
  switch (drive) {
    case FEED_REEL:
      reels.run(dir, speed, FEED);
      break;
    case FEED_PINCH:
      pinches.run(dir, speed, FEED);
      break;
    case PICKUP_REEL:
      reels.run(dir, speed, PICKUP);
      break;
    case PICKUP_PINCH:
      pinches.run(dir, speed, PICKUP);
      break;
    default:
      error(ERR_INVALID_DRIVE);
  }
}

void set_speed(byte drive, float speed) {
  switch (drive) {
    case FEED_REEL:
      reels.setMaxSpeed(speed, FEED);
      break;
    case FEED_PINCH:
      pinches.setMaxSpeed(speed, FEED);
      break;
    case PICKUP_REEL:
      reels.setMaxSpeed(speed, PICKUP);
      break;
    case PICKUP_PINCH:
      pinches.setMaxSpeed(speed, PICKUP);
      break;
    default:
      error(ERR_INVALID_DRIVE);
  }
}

void set_speed(CommandProtocol *cmd) {
  // check type, check side
  if (!cmd->has_arg()) {
    error(ERR_MISSING_ARG);
    return;
  }
  byte drive = cmd->get_arg<byte>();
  if (!cmd->has_arg()) {
    error(ERR_MISSING_ARG);
    return;
  }
  float speed = cmd->get_arg<float>();
  set_speed(drive, speed);
}

void get_speed(CommandProtocol *cmd) {
  if (!cmd->has_arg()) {
    error(ERR_MISSING_ARG);
    return;
  }
  // check type, check side
  float s = 0;
  switch (cmd->get_arg<byte>()) {
    case FEED_REEL:
      s = reels.getMaxSpeed(FEED);
      break;
    case FEED_PINCH:
      s = pinches.getMaxSpeed(FEED);
      break;
    case PICKUP_REEL:
      s = reels.getMaxSpeed(PICKUP);
      break;
    case PICKUP_PINCH:
      s = pinches.getMaxSpeed(PICKUP);
      break;
    default:
      error(ERR_INVALID_DRIVE);
  }
  cmd->start_command(CMD_GET_SPEED);
  cmd->add_arg(s);
  cmd->finish_command();
}

void move_drive(CommandProtocol *cmd) {
  if (!cmd->has_arg()) {
    error(ERR_MISSING_ARG);
    return;
  }
  // check type, check side
  byte drive = cmd->get_arg<byte>();
  if (!cmd->has_arg()) {
    error(ERR_MISSING_ARG);
    return;
  }
  byte dir = cmd->get_arg<byte>();
  if ((dir != 0) && (dir != 1)) {
    error(ERR_INVALID_ARG);
    return;
  }
  if (!cmd->has_arg()) {
    error(ERR_MISSING_ARG);
    return;
  }
  unsigned long n_steps = cmd->get_arg<unsigned long>();
  switch (drive) {
    case FEED_REEL:
      reels.move(dir, n_steps, FEED);
      break;
    case FEED_PINCH:
      pinches.move(dir, n_steps, FEED);
      break;
    case PICKUP_REEL:
      reels.move(dir, n_steps, PICKUP);
      break;
    case PICKUP_PINCH:
      pinches.move(dir, n_steps, PICKUP);
      break;
    default:
      error(ERR_INVALID_DRIVE);
  }
}

void run_reels(float speed) {
  reels.run(1, speed, FEED);
  reels.run(0, speed, PICKUP);
}

void run_reels(CommandProtocol *cmd) {
  if (!cmd->has_arg()) {
    error(ERR_MISSING_ARG);
    return;
  }
  float speed = cmd->get_arg<float>();
  run_reels(speed);
}

void stop_reels() {
  reels.softHiZ();
}

void stop_reels(CommandProtocol *cmd) {
  stop_reels();
}

void stop_all(CommandProtocol *cmd) {
  reels.softHiZ();
  pinches.softStop();
}

void release_all() {
  reels.softHiZ();
  pinches.softHiZ();
}

void release_all(CommandProtocol *cmd) {
  release_all();
}

void halt_all() {
  reels.hardHiZ();
  pinches.hardHiZ();
}

void halt_all(CommandProtocol *cmd) {
  halt_all();
}

void wait_for_pinch_drives() {
  while(pinches.getBusy());
  return;
}

byte wait_for_pinch_drives_and_watch_tension(long *tension) {
  long t = 0;
  while(pinches.getBusy()) {
    t = read_tension();
    if ((t > tension_high_limit) | (t < tension_low_limit)) {
      error(ERR_TENSION);
      halt_all();
      *tension = t;
      return 1;
    }
  }
  *tension = t;
  return 0;
}
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

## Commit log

2019-10-02 adding initial set of files
    [parts.xlsx, pinouts.xlsx]
2019-10-02 adding BOM
    [BOM_191002.xlsx]
2019-10-02 adding CAD and part drawings
    [100517 render.sldprt, 100g_load_cell_RB-Phi-203.SLDPRT, 101649 render.sldprt, 101920 render.sldprt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]
2020-02-05 Adding missing files
    [picam_to_viewport_mount.SLDPRT, tc_led_mount.SLDPRT]
2020-02-05 Updating BOM for new files
    [BOM_191002.xlsx]
2023-11-14 Updated BOM and reel mounts, added half of the slip clutch modifications.
    [BOM_191002.xlsx, SI_sdpsi_s98ca6-mec160417.SLDDRW, SI_sdpsi_s98ca6-mec160417.stp, bandbmnfg_18mp012-6fa2.SLDPRT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]
2023-11-18 added the rest of the slip clutch CAD variation edits
    [reel_drive_clamp_slipclutch.SLDPRT, shaft_adapter_slipclutch.SLDDRW, shaft_adapter_slipclutch.SLDPRT]
2023-11-21 updated the BOM to reflect the slip clutch CAD modifcations and to add slip clutch CAD hardware
    [BOM_191002.xlsx]
2023-11-21 updated gridtape assembly to include slip clutch, updated assembly documentation
    [100517 render.sldprt, 100g_load_cell_RB-Phi-203.SLDPRT, 101649 render.sldprt, 101920 render.sldprt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]
2023-11-30 edited the BOM date and changed the takeup_rest to be made out of stainless steel
    [BOM_191002.xlsx, BOM_231129.xlsx]
2024-01-11 updated gridtape assembly instructions
